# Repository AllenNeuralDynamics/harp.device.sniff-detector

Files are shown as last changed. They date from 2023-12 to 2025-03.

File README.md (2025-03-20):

Analog Front-End for an implanted 22KOhm thermistor.

## Features:
* 1Hz highpass filter
* 1KHz lowpass filter
* Vout = 1.65 + 100\*Vin
* Common mode thermistor input filtering
* Common mode supply voltage filtering

## Wiring Diagram
TODO

## Additional Parts
These parts aren't part of the PCBA, but they are required for a complete sensing solution:

* 22kOhm thermsistor PN: GAG22K7MCD419 [digikey link](https://www.digikey.com/en/products/detail/te-connectivity-measurement-specialties/GAG22K7MCD419/5277253)
* Flexible 2-conductor 36AWG Shielded TAU cable PN: TAU-3607.02 [link](https://www.micronmeters.com/product/tau-cable-36-awg)
* 2-Pin Molex Connector Plug PN: 0533984002 ([link](https://www.digikey.com/en/products/detail/molex/0533984002/15622916))
* 2-Pin Molex Connector Socket PN: 0151340206 ([link](https://www.digikey.com/en/products/detail/molex/0151340206/6198199))

### Old Connectors
These connectors are no longer used:
* 2-pin Mill Max Connector pins PN: 850-10-002-20-001000 [digikey link](https://www.digikey.com/en/products/detail/mill-max-manufacturing-corp/800-10-002-20-001000/7762570)
* 2-socket Mill Max Connector socket PN: 801-47-002-10-012000 [digikey link](https://www.digikey.com/en/products/detail/mill-max-manufacturing-corp/801-47-002-10-012000/7364072)

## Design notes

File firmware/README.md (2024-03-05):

## Setting up the Build Environment

### Install Submodules
This project uses [Harp Core RP2040](https://github.com/AllenNeuralDynamics/harp.core.rp2040) and [etl](https://github.com/ETLCPP/etl/tree/master) libraries as submodules.
Install it with:
````
git submodule update --init
````

### Install Pico SDK
This project uses the [Pico SDK](https://github.com/raspberrypi/pico-sdk/tree/master).
The SDK needs to be downloaded and installed to a known folder on your PC.
Note that the PICO SDK also contains submodules (including TinyUSB), so you must ensure that they are also fetched with:
````
git clone git clone git@github.com:raspberrypi/pico-sdk.git
git submodule update --init --recursive
````

### Point to Pico SDK
Recommended, but optional: define the `PICO_SDK_PATH` environment variable to point to the location where the pico-sdk was downloaded. i.e:
````
PICO_SDK_PATH=/home/username/projects/pico-sdk
````
On Linux, it may be preferrable to put this in your `.bashrc` file.

## Compiling the Firmware

### Without an IDE
From this directory, create a directory called build, enter it, and invoke cmake with:
````
mkdir build
cd build
cmake ..
````
If you did not define the `PICO_SDK_PATH` as an environment variable, you must pass it in here like so:
````
mkdir build
cd build
cmake -DPICO_SDK_PATH=/path/to/pico-sdk ..
````
After this point, you can invoke the auto-generated Makefile with `make`

## Flashing the Firmware
Press-and-hold the Pico's BOOTSEL button and power it up (i.e: plug it into usb).
At this point you do one of the following:
* drag-and-drop the created **\*.uf2** file into the mass storage device that appears on your pc.
* flash with [picotool](https://github.com/raspberrypi/picotool)

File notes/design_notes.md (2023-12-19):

## References
* [Shibaura Thermistors](https://www.shibauraelectronics.com/pdf/shibaura_products_catalog.pdf)
    * Overview of thermistor principles
* [Thermistor Temperature Sensing System](https://www.analog.com/en/analog-dialogue/articles/thermistor-temperature-sensing-system-part-1.html)
* [Thermistor Interfacing](https://www.analog.com/media/en/training-seminars/design-handbooks/transducer-interfacing-handbook/Chapter9.pdf)
* [QR Code Generator](https://www.the-qrcode-generator.com/)
* [Hammond Manufacturing enclosure dimensions](https://www.hammfg.com/files/parts/pdf/1455C801.pdf)
## Self-Heating Strategy References
* [LM134 Datasheet](https://www.analog.com/media/en/technical-documentation/data-sheets/134sfc.pdf)
    * Constant current source for self-heating strategy (See "Zero Temperature Coefficient Current Source".)
* [Thermal Anemometers](http://www.fonema.se/anemom/anemom.html)
* [Constant Current Hot-Wire Anemometer](https://forum.allaboutcircuits.com/threads/constant-current-hot-wire-anemometer.63204/page-2#post-432202)
* [Thermistor for Simple Breath Detector](https://forum.allaboutcircuits.com/threads/thermistor-for-simple-breath-detector.173203/)
* [Differential and Common Mode Noise](https://www.murata.com/~/media/webrenewal/products/emc/emifil/knowhow/26to30.ashx)

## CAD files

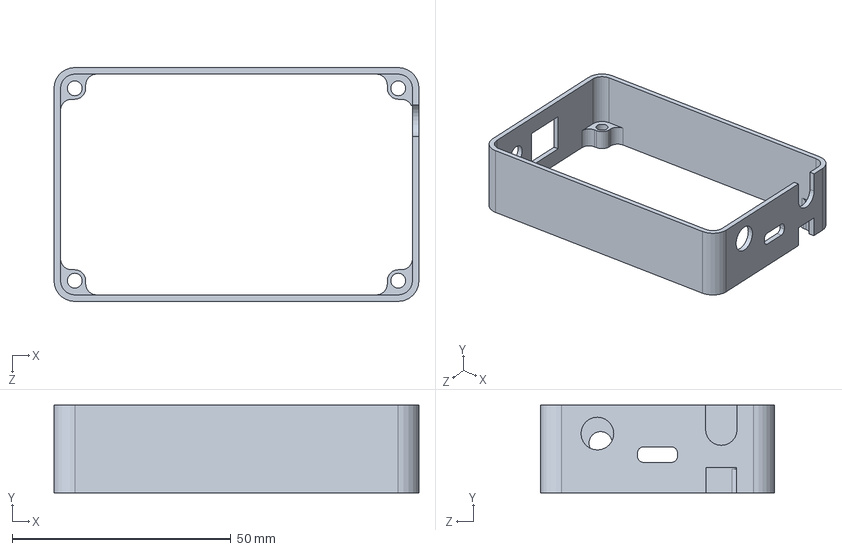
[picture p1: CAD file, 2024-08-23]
hardware/enclosure/cads/solidworks/sniff_detector_enclosure.SLDPRT
83.5 x 20.1 x 53.5 mm

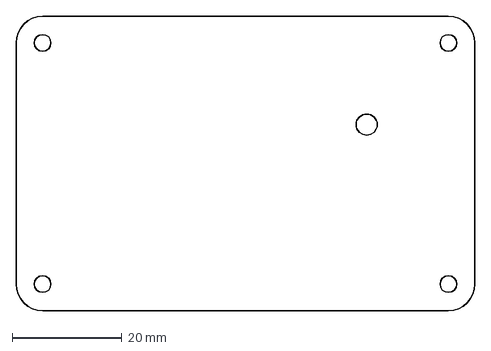
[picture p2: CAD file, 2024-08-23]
hardware/enclosure/exports/dxfs/sniff_detector_enclosure_lid_top_offset.DXF
83.7 x 53.7 mm

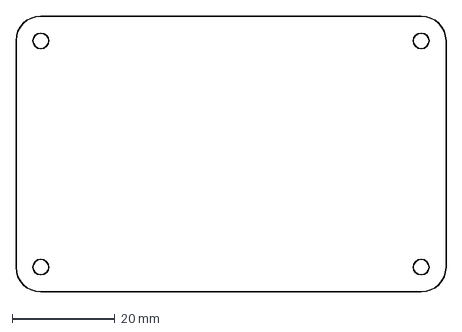
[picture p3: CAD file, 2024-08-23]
hardware/enclosure/exports/dxfs/sniff_detector_enclosure_lid_bottom_offset.DXF
83.7 x 53.7 mm

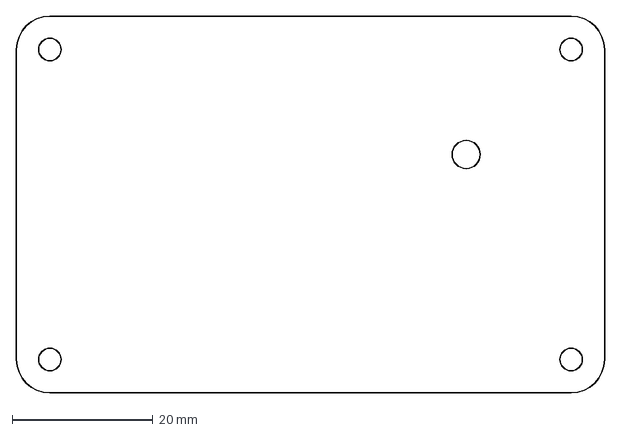
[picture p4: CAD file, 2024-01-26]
hardware/enclosure/exports/dxfs/sniff_detector_enclosure_lid_top.DXF
83.5 x 53.5 mm

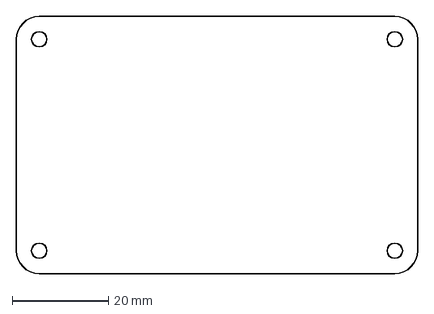
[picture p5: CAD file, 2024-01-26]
hardware/enclosure/exports/dxfs/sniff_detector_enclosure_lid_bottom.DXF
83.5 x 53.5 mm

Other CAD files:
hardware/enclosure/exports/stls/sniff_detector_sides_enclosure.STL

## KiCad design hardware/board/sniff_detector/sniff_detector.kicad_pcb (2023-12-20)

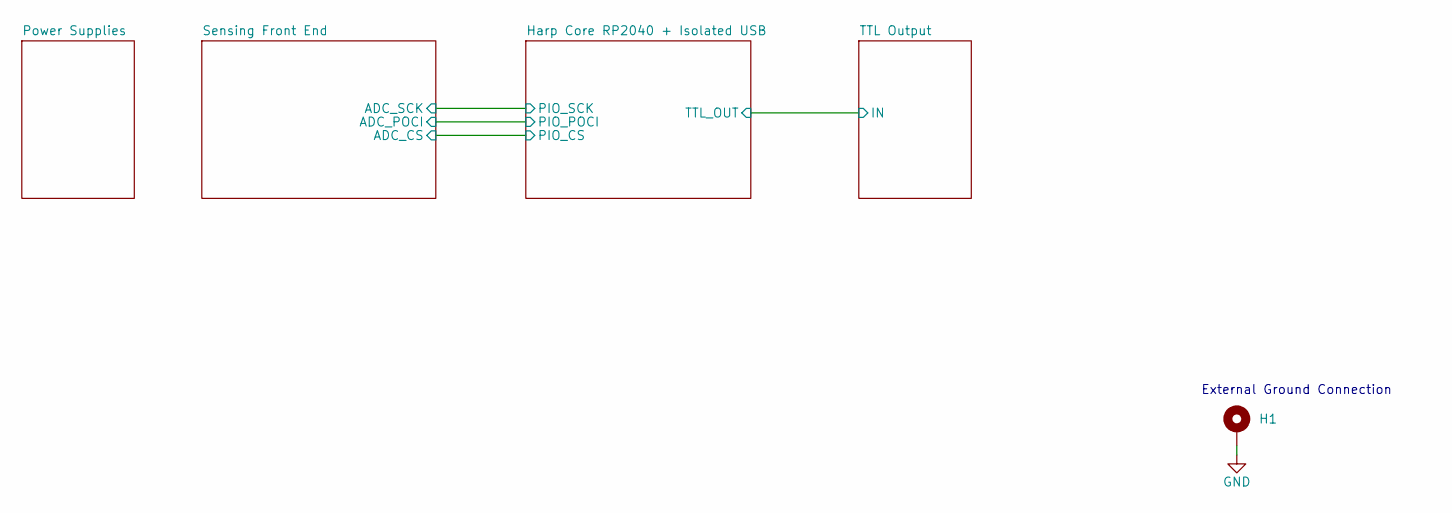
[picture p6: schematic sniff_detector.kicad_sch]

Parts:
H1: MountingHole_Pad; Terminal_Keystone_779x_EdgeMount_Horizontal

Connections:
GND: H1.1; also elsewhere on the board

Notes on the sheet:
External Ground Connection

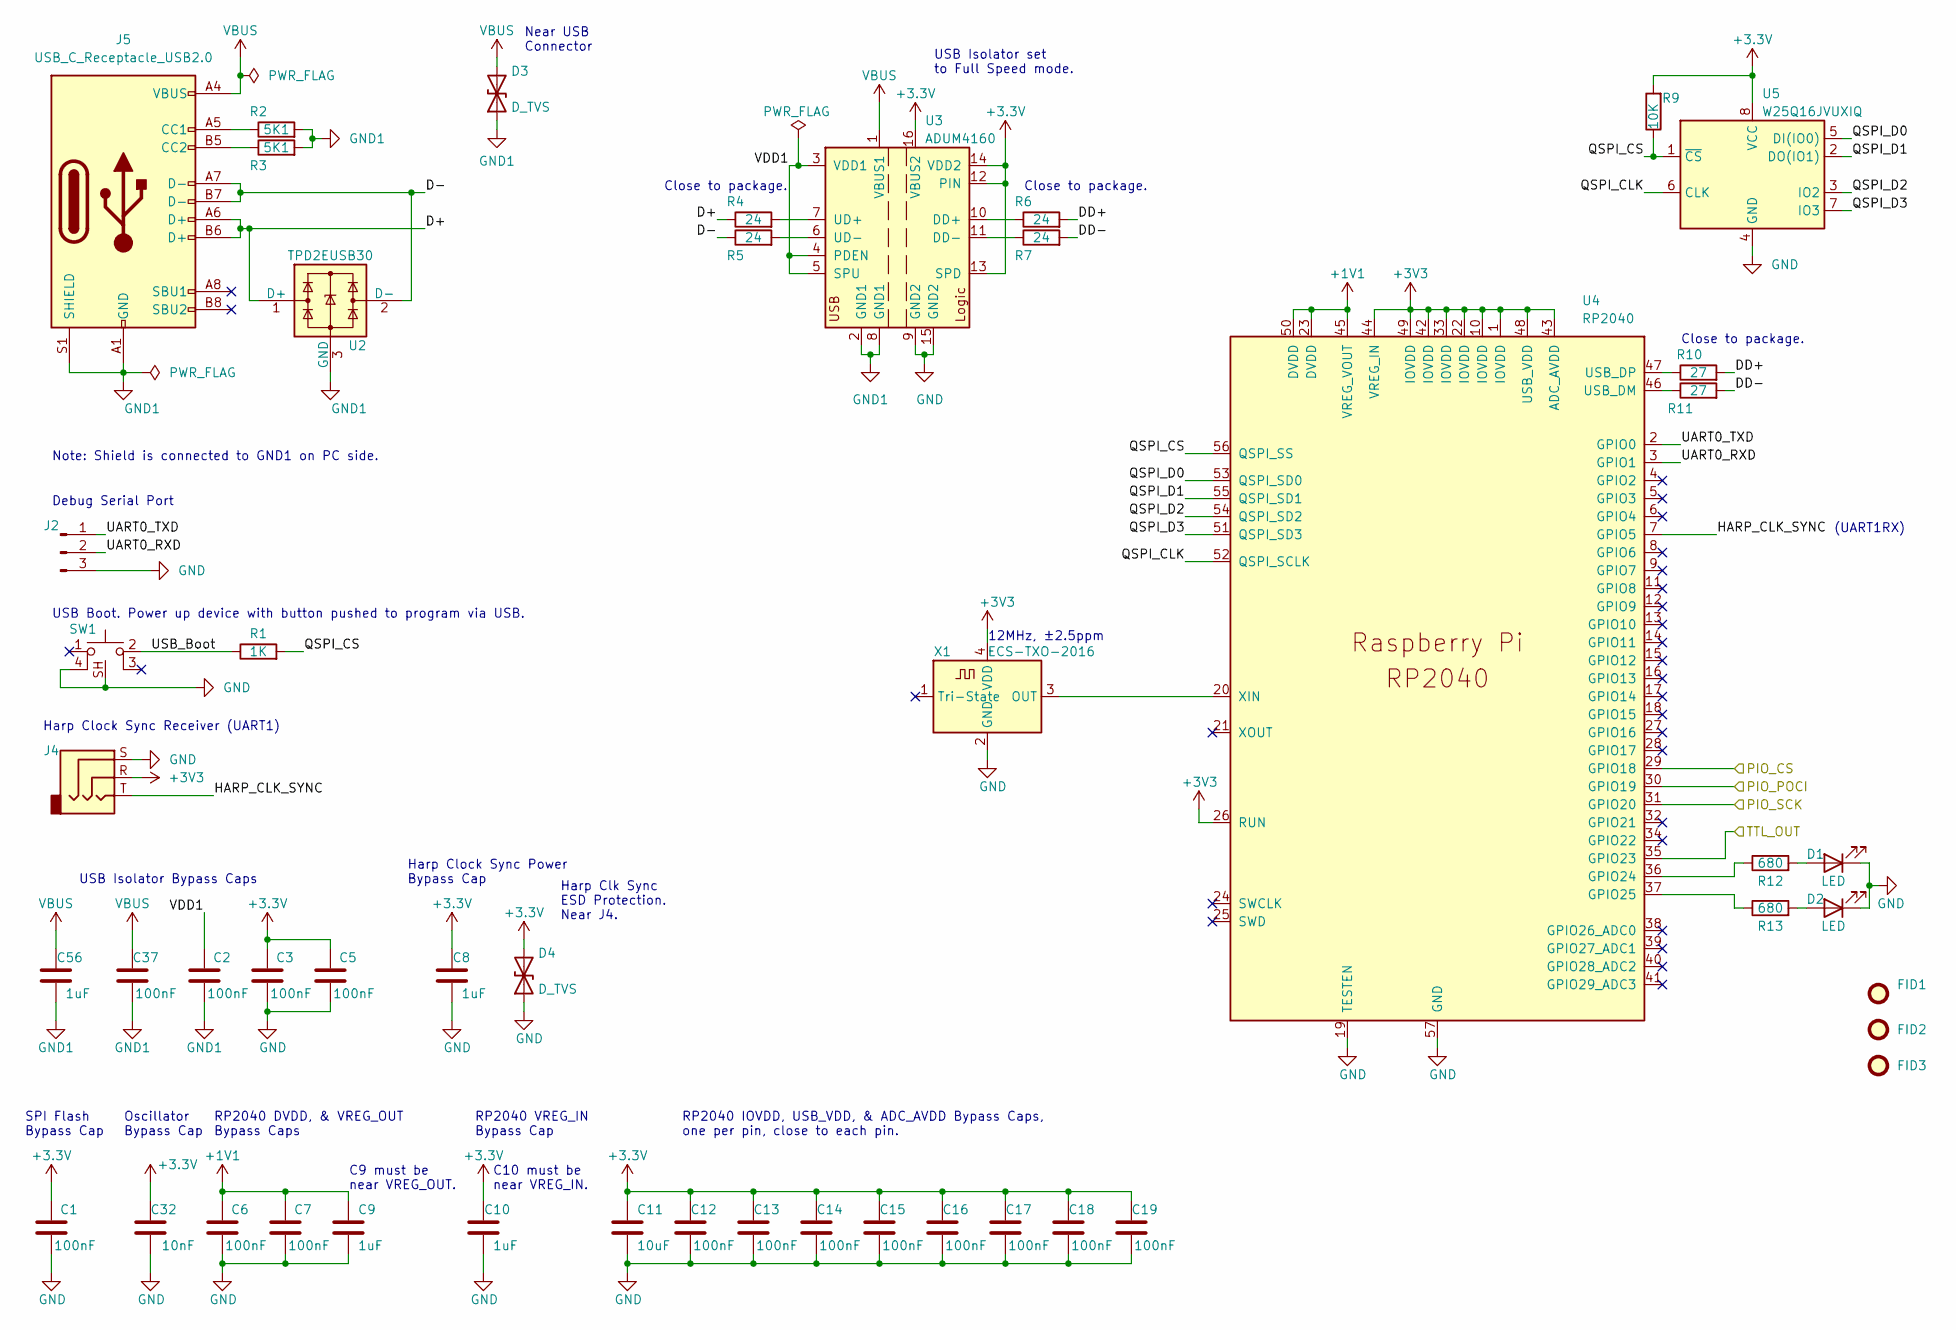
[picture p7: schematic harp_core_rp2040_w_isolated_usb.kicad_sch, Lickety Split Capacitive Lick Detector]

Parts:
C1, C2, C3, C5, C6, C7, C12, C13, C14, C15, C16, C17, C18, C19, C37: 100nF; C_0402_1005Metric; Rated Voltage 16V; Tolerance 10%
C8, C9, C10, C56: 1uF; C_0402_1005Metric; Rated Voltage 35V; Voltage 35V
C11: 10uF; C_0603_1608Metric; Rated Voltage 25V; Tolerance 10%
C32: 10nF; C_0402_1005Metric; Rated Voltage 25V; Tolerance 10%
D1, D2: LED; LED_0603_1608Metric_Pad1.05x0.95mm_HandSolder
D3, D4: D_TVS; D_0402_1005Metric
FID1, FID2, FID3: Fiducial; Fiducial_0.5mm_Mask1mm
J2: Conn_01x03_Male; PinHeader_1x03_P2.54mm_Vertical
J4: AudioJack3; Jack_3.5mm_CUI_SJ-3523-SMT_Horizontal
J5: USB_C_Receptacle_USB2.0; USB_C_Receptacle_JAE_DX07S016JA1R1500
R1: 1K; R_0402_1005Metric; Tolerance 1%
R2, R3: 5K1; R_0402_1005Metric; Tolerance 1%
R4, R5, R6, R7: 24; R_0402_1005Metric; Tolerance 1%
R9: 10K; R_0402_1005Metric
R10, R11: 27; R_0402_1005Metric; Tolerance 1%
R12, R13: 680; R_0402_1005Metric; Tolerance 1%
SW1: SW_Push_1P1T-SH_NO_Vertical_Wuerth_WS-TASV
U2: TPD2EUSB30; Texas_DRT-3
U3: ADUM4160; SOIC-16W_7.5x10.3mm_P1.27mm
U4: RP2040; RP2040-QFN-56
U5: W25Q16JVUXIQ; Winbond-8USON-2x3mm
X1: ECS-TXO-2016; Crystal_SMD_2016-4Pin_2.0x1.6mm; Tolerance ±2.5ppm

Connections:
+1V1: C6.2, C7.2, C9.1, U4.23 (DVDD), U4.45 (VREG_VOUT), U4.50 (DVDD)
/Harp Core RP2040 + Isolated USB/D+: J5.A6 (D+), J5.B6 (D+), R4.1, U2.1 (D+)
/Harp Core RP2040 + Isolated USB/D-: J5.A7 (D-), J5.B7 (D-), R5.1, U2.2 (D-)
/Harp Core RP2040 + Isolated USB/DD+: R6.2, R10.2
/Harp Core RP2040 + Isolated USB/DD-: R7.2, R11.2
/Harp Core RP2040 + Isolated USB/HARP_CLK_SYNC: J4.T, U4.7 (GPIO5)
/Harp Core RP2040 + Isolated USB/PIO_CS: U4.29 (GPIO18); also elsewhere on the board
/Harp Core RP2040 + Isolated USB/PIO_POCI: U4.30 (GPIO19); also elsewhere on the board
/Harp Core RP2040 + Isolated USB/PIO_SCK: U4.31 (GPIO20); also elsewhere on the board
/Harp Core RP2040 + Isolated USB/QSPI_CLK: U4.52 (QSPI_SCLK), U5.6 (CLK)
/Harp Core RP2040 + Isolated USB/QSPI_CS: R1.2, R9.1, U4.56 (QSPI_SS), U5.1 (~CS)
/Harp Core RP2040 + Isolated USB/QSPI_D0: U4.53 (QSPI_SD0), U5.5 (DI(IO0))
/Harp Core RP2040 + Isolated USB/QSPI_D1: U4.55 (QSPI_SD1), U5.2 (DO(IO1))
/Harp Core RP2040 + Isolated USB/QSPI_D2: U4.54 (QSPI_SD2), U5.3 (IO2)
/Harp Core RP2040 + Isolated USB/QSPI_D3: U4.51 (QSPI_SD3), U5.7 (IO3)
/Harp Core RP2040 + Isolated USB/TTL_OUT: U4.35 (GPIO23); also elsewhere on the board
/Harp Core RP2040 + Isolated USB/UART0_RXD: J2.2, U4.3 (GPIO1)
/Harp Core RP2040 + Isolated USB/UART0_TXD: J2.1, U4.2 (GPIO0)
/Harp Core RP2040 + Isolated USB/USB_Boot: R1.1, SW1.2
/Harp Core RP2040 + Isolated USB/VDD1: C2.2, U3.3 (VDD1), U3.4 (PDEN), U3.5 (SPU)
GND: C1.1, C3.1, C5.1, C6.1, C7.1, C8.2, C9.2, C10.2, C11.2, C12.1, C13.1, C14.1, C15.1, C16.1, C17.1, C18.1, C19.1, C32.1, D1.1 (K), D2.1 (K), D4.1 (A1), J2.3, J4.S, SW1.4, SW1.SH, U3.9 (GND2), U3.15 (GND2), U4.19 (TESTEN), U4.57 (GND), U5.4 (GND), X1.2 (GND); also elsewhere on the board
GND1: C2.1, C37.1, C56.2, D3.1 (A1), J5.A1 (GND), J5.A12 (GND), J5.B1 (GND), J5.B12 (GND), J5.S1 (SHIELD), R2.2, R3.2, U2.3 (GND), U3.2 (GND1), U3.8 (GND1)
unnamed: D1.2 (A), R12.2
unnamed: D2.2 (A), R13.2
unnamed: J5.A5 (CC1), R2.1
unnamed: J5.B5 (CC2), R3.1
unnamed: R6.1, U3.10 (DD+)
unnamed: R7.1, U3.11 (DD-)
unnamed: R4.2, U3.7 (UD+)
unnamed: R5.2, U3.6 (UD-)
unnamed: R12.1, U4.36 (GPIO24)
unnamed: R13.1, U4.37 (GPIO25)
unnamed: R11.1, U4.46 (USB_DM)
unnamed: R10.1, U4.47 (USB_DP)
unnamed: U4.20 (XIN), X1.3 (OUT)
VBUS: C37.2, C56.1, D3.2 (A2), J5.A4 (VBUS), J5.A9 (VBUS), J5.B4 (VBUS), J5.B9 (VBUS), U3.1 (VBUS1)

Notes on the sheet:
Close to package.
Near USB Connector
(UART1RX)
Harp Clk Sync ESD Protection. Near J4.
RP2040 VREG_IN Bypass Cap
Oscillator Bypass Cap
Harp Clock Sync Power Bypass Cap
C10 must be near VREG_IN.
RP2040 DVDD, & VREG_OUT Bypass Caps
Debug Serial Port
USB Boot. Power up device with button pushed to program via USB.
C9 must be near VREG_OUT.
Harp Clock Sync Receiver (UART1)
12MHz, ±2.5ppm
Note: Shield is connected to GND1 on PC side.
RP2040 IOVDD, USB_VDD, & ADC_AVDD Bypass Caps, one per pin, close to each pin.
USB Isolator Bypass Caps
SPI Flash Bypass Cap
USB Isolator set to Full Speed mode.

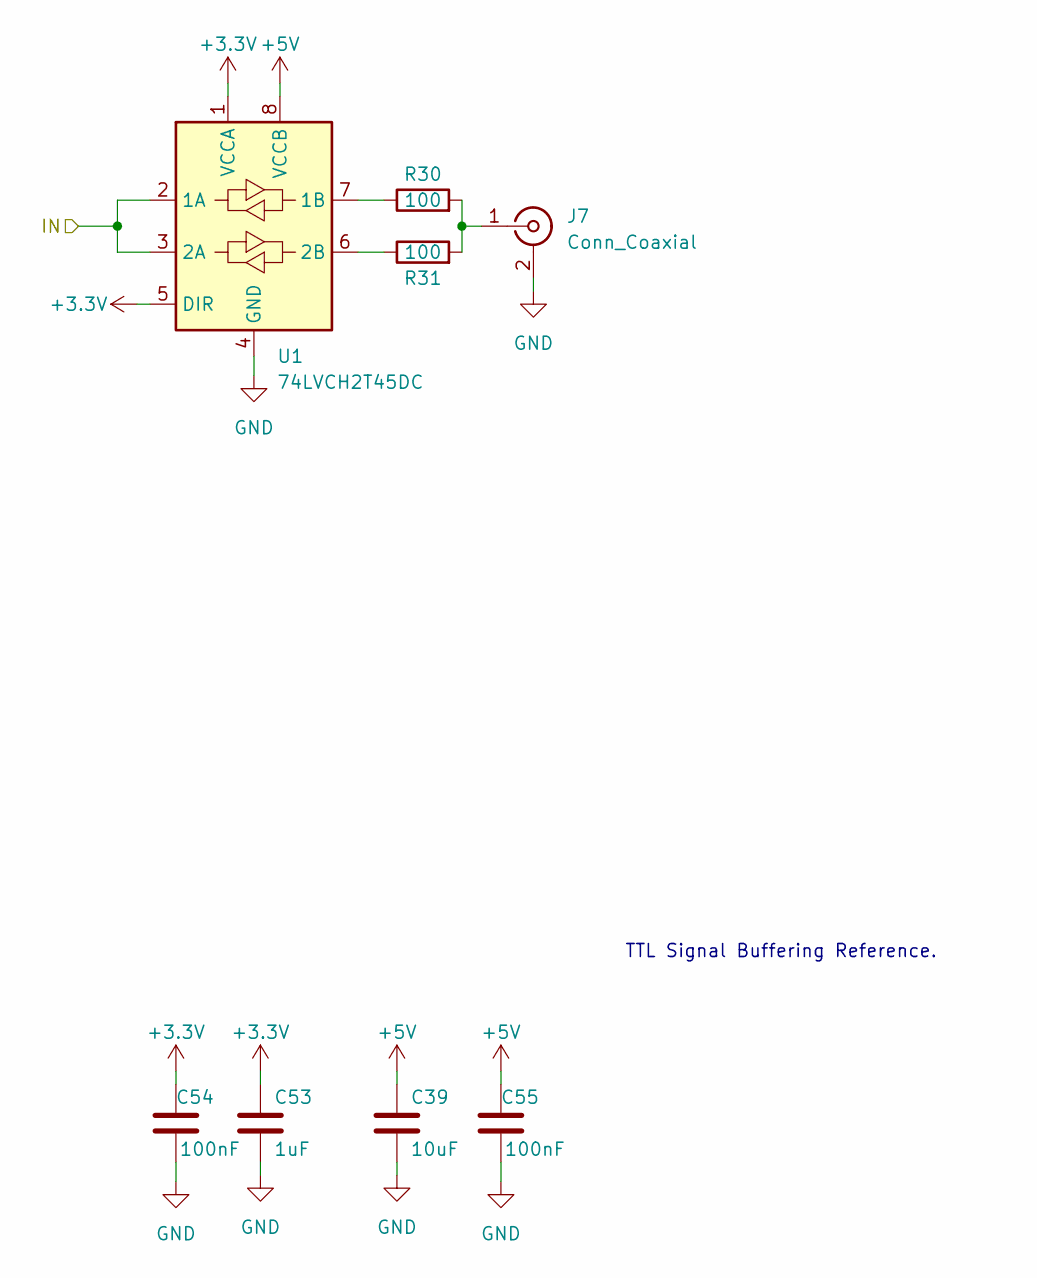
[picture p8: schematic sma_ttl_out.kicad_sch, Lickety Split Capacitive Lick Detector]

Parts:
C39: 10uF; C_0603_1608Metric; Rated Voltage 25V; Tolerance 10%
C53: 1uF; C_0402_1005Metric; Rated Voltage 35V; Voltage 35V
C54, C55: 100nF; C_0402_1005Metric; Rated Voltage 16V; Tolerance 10%
J7: Conn_Coaxial; SMA_TE_Connectivity_CONSMA002-SMD-G-T_Horizontal
R30, R31: 100; R_0603_1608Metric_Pad0.98x0.95mm_HandSolder; Tolerance 1%
U1: 74LVCH2T45DC; VSSOP-8_2.3x2mm_P0.5mm

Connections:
+5V: C39.1, C55.2, U1.8 (VCCB); also elsewhere on the board
/Harp Core RP2040 + Isolated USB/TTL_OUT: U1.2 (1A), U1.3 (2A); also elsewhere on the board
GND: C39.2, C53.2, C54.1, C55.1, J7.2 (Ext), U1.4 (GND); also elsewhere on the board
unnamed: J7.1 (In), R30.2, R31.2
unnamed: R30.1, U1.7 (1B)
unnamed: R31.1, U1.6 (2B)

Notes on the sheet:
TTL Signal Buffering Reference.

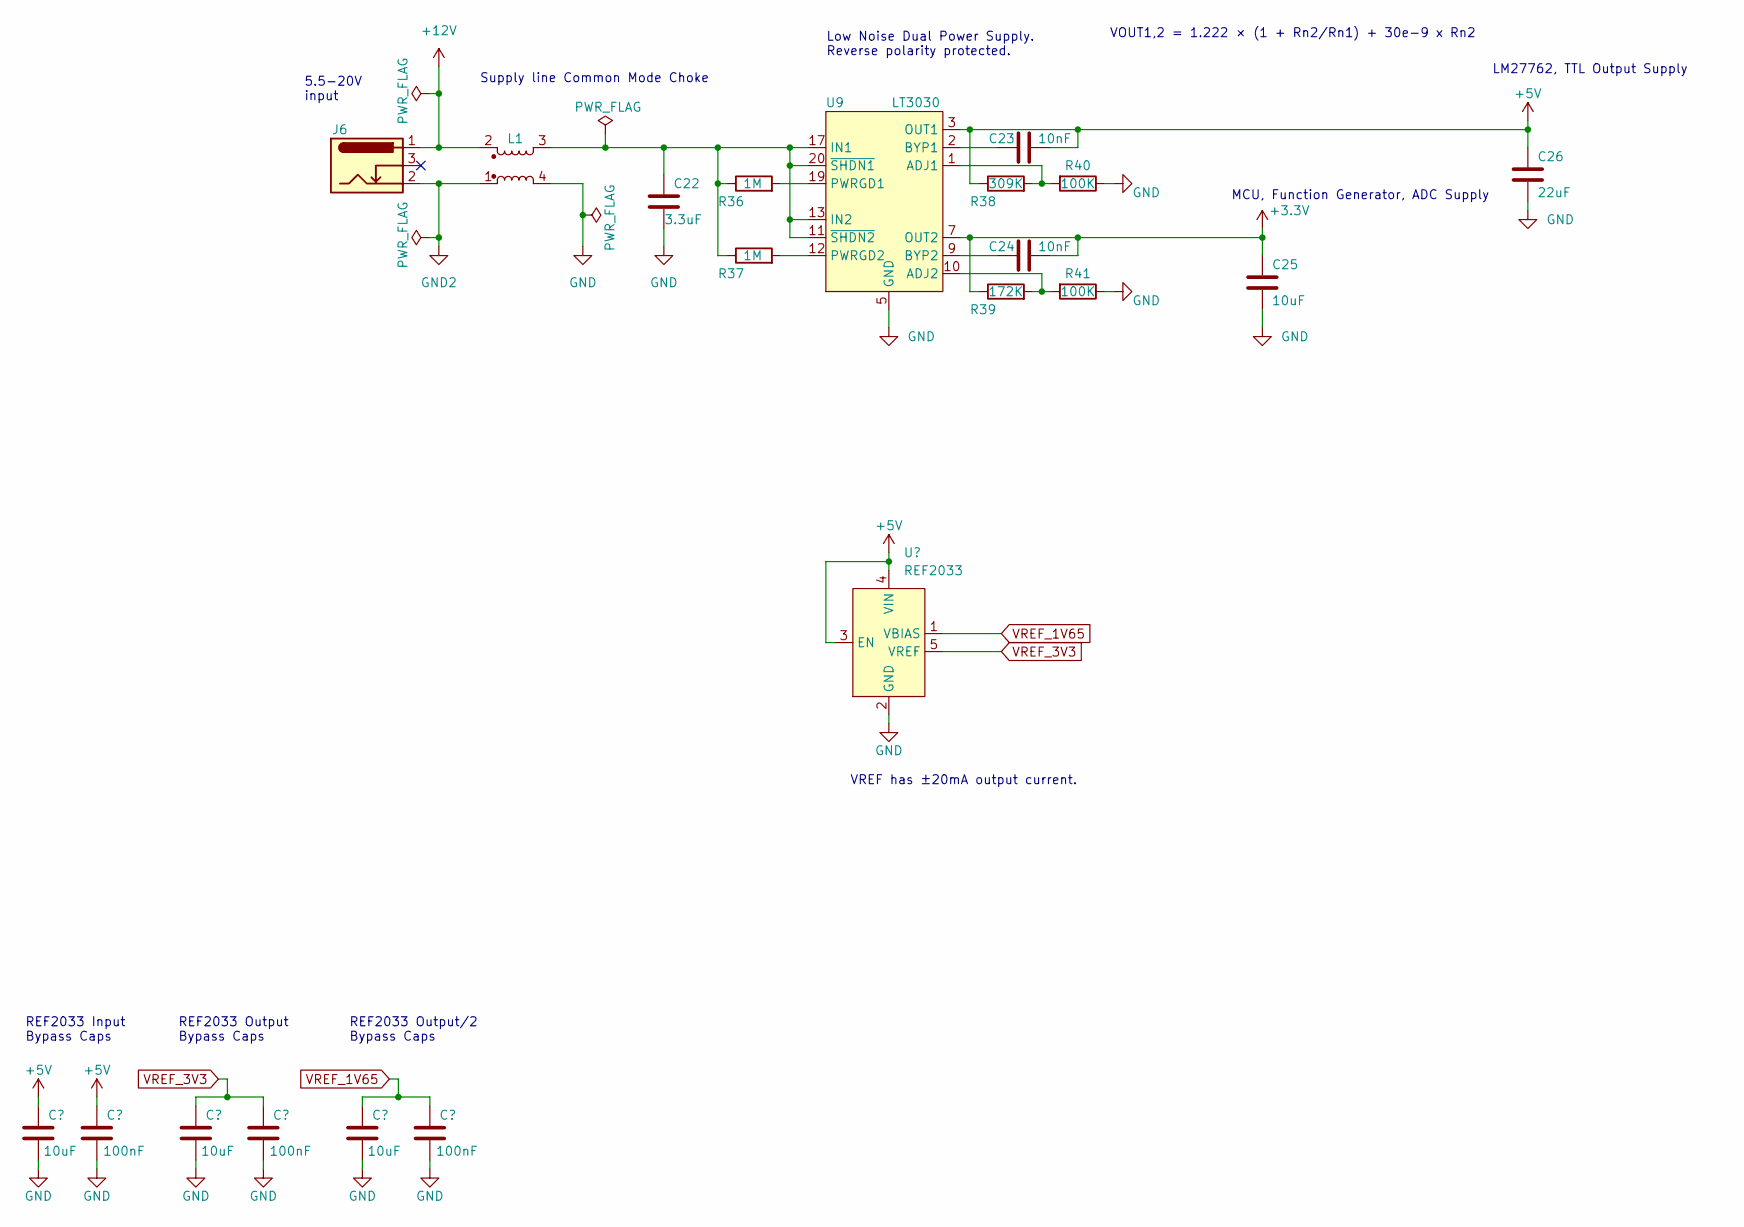
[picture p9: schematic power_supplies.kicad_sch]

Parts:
C22: 3.3uF; C_0805_2012Metric; Rated Voltage 25V; Tolerance 10%
C23, C24: 10nF; C_0402_1005Metric; Rated Voltage 25V; Tolerance 10%
C25: 10uF; C_0603_1608Metric; Rated Voltage 25V; Tolerance 10%
C26: 22uF; C_0805_2012Metric; Rated Voltage 25V; Voltage 25V
C35, C38, C41: 10uF; C_0603_1608Metric; Tolerance 10%; Voltage 25V
C36, C40, C42: 100nF; C_0402_1005Metric; Tolerance 10%; Voltage 16V
J6: Barrel_Jack_Switch; BarrelJack_CUI_PJ-102AH_Horizontal
L1: L_Coupled_1423; L_CommonModeChoke_TDKCorporation_1210
R36, R37: 1M; R_0402_1005Metric; Tolerance 1%
R38: 309K; R_0402_1005Metric; Tolerance 0.1%
R39: 172K; R_0402_1005Metric; Tolerance 1%
R40, R41: 100K; R_0402_1005Metric; Tolerance 0.1%
U8: REF2033; SOT-23-5
U9: LT3030; ETSSOP-20-1EP_4.4x6.5mm_P0.65mm_EP3x4.2mm

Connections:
+5V: C23.1, C26.1, C35.1, C36.2, R38.1, U8.3 (EN), U8.4 (VIN), U9.3 (OUT1), U9.4 (OUT1); also elsewhere on the board
+12V: J6.1, L1.2
GND: C22.2, C25.2, C26.2, C35.2, C36.1, C38.2, C40.1, C41.2, C42.1, L1.4, R40.1, R41.1, U8.2 (GND), U9.5 (GND), U9.6 (GND), U9.15 (GND), U9.16 (GND), U9.21 (GND); also elsewhere on the board
GND2: J6.2, L1.1
IN1: C22.1, L1.3, R36.1, R37.1, U9.11 (~SHDN2), U9.13 (IN2), U9.14 (IN2), U9.17 (IN1), U9.18 (IN1), U9.20 (~SHDN1)
unnamed: R38.2, R40.2, U9.1 (ADJ1)
unnamed: R39.2, R41.2, U9.10 (ADJ2)
unnamed: C23.2, U9.2 (BYP1)
unnamed: C24.2, U9.9 (BYP2)
unnamed: R36.2, U9.19 (PWRGD1)
unnamed: R37.2, U9.12 (PWRGD2)
VREF_1V65: C41.1, C42.2, U8.1 (VBIAS); also elsewhere on the board
VREF_3V3: C38.1, C40.2, U8.5 (VREF); also elsewhere on the board

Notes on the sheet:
REF2033 Input Bypass Caps
REF2033 Output/2 Bypass Caps
MCU, Function Generator, ADC Supply
5.5-20V input
REF2033 Output Bypass Caps
VOUT1,2 = 1.222 × (1 + Rn2/Rn1) + 30e-9 x Rn2
Supply line Common Mode Choke
VREF has ±20mA output current.
Low Noise Dual Power Supply. Reverse polarity protected.
LM27762, TTL Output Supply

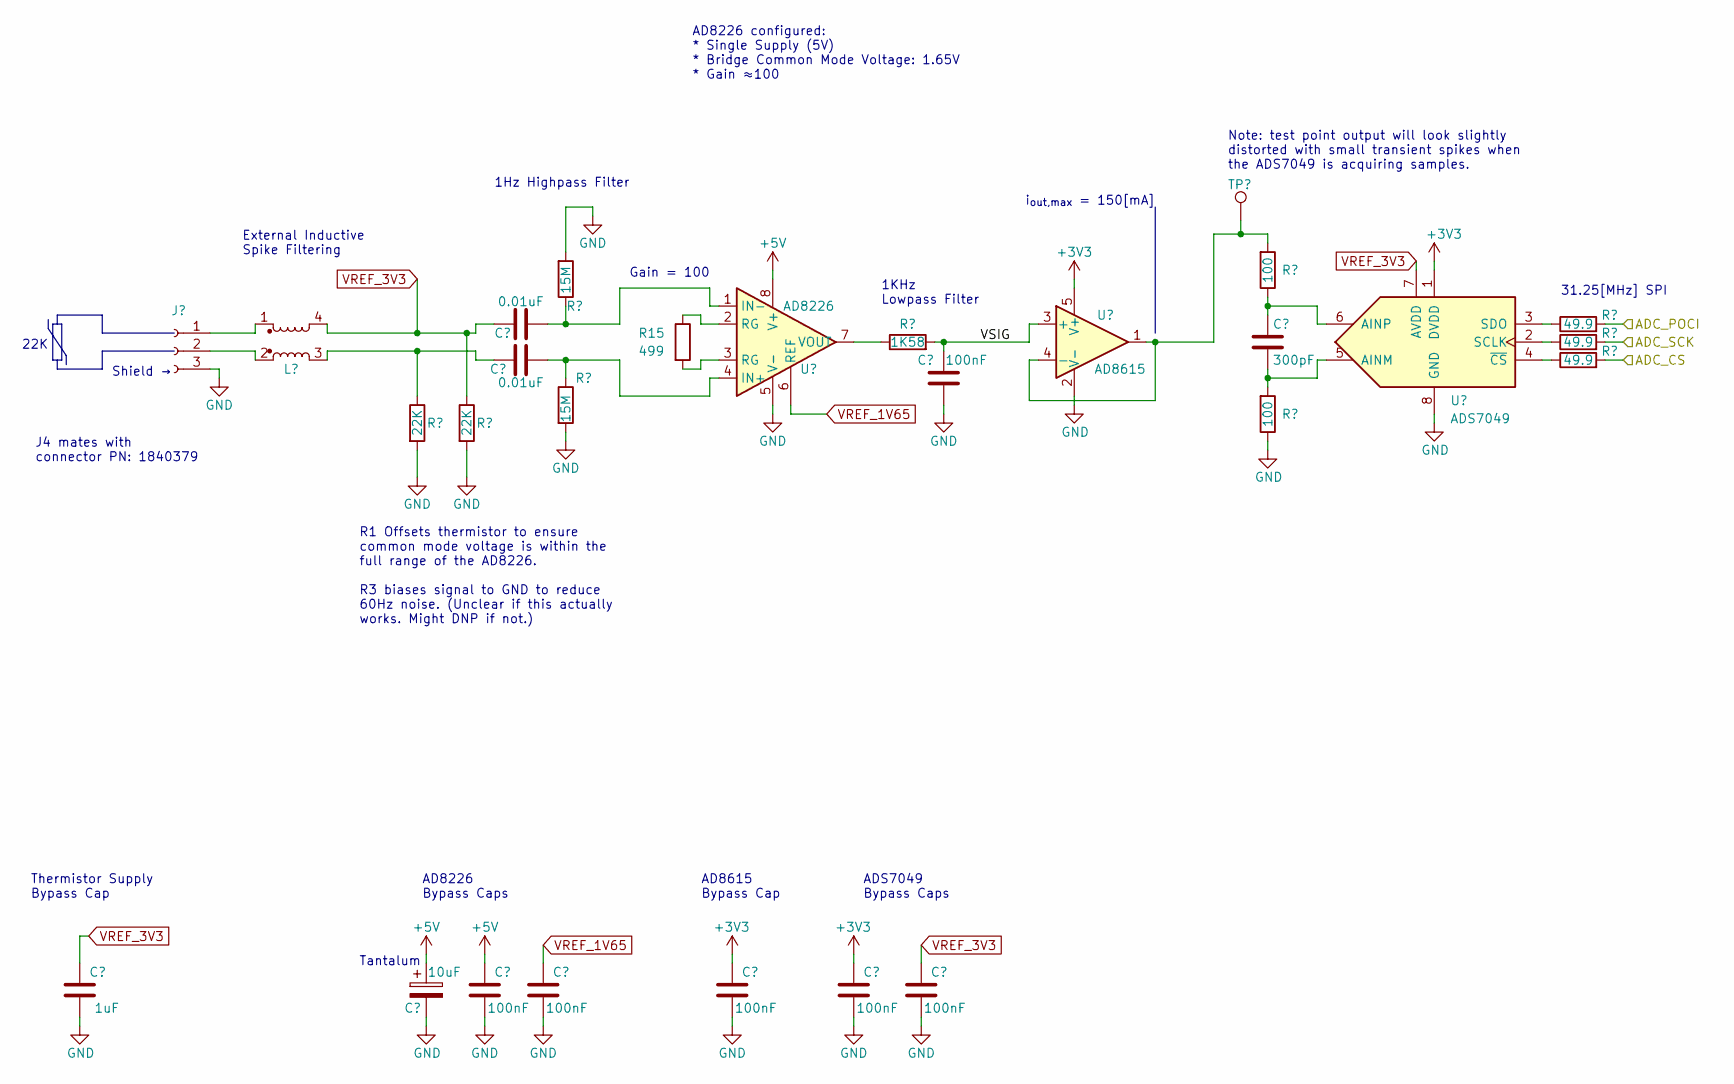
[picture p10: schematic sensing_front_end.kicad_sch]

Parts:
C4: 1uF; C_0402_1005Metric; Voltage 35V; Rated Voltage 35V
C20: 10uF; C_0805_2012Metric; Rated Voltage 10V; Tolerance 20%
C21, C29, C30, C31, C33: 100nF; C_0402_1005Metric; Rated Voltage 16V; Tolerance 10%
C27, C28: 0.01uF; C_1206_3216Metric; Tolerance 1%
C34: 100nF; C_0402_1005Metric; Tolerance 10%; Voltage 16V
C52: 300pF; C_0402_1005Metric; Tolerance 1%
J1: Conn_01x03_Female; PhoenixContact_MC_1,5_3-G-3.5_1x03_P3.50mm_Horizontal
L2: L_Coupled_1423; L_CommonModeChoke_TDKCorporation_1210
R8, R18: 22K; R_0603_1608Metric; Tolerance 0.1%
R14, R17: 15M; R_1206_3216Metric; Tolerance 1%
R15: 499; R_0603_1608Metric_Pad0.98x0.95mm_HandSolder; Tolerance 0.1%
R16: 1K58; R_0603_1608Metric; Tolerance 0.1%
R28, R29, R44: 49.9; R_0402_1005Metric
R42, R43: 100; R_0402_1005Metric; Tolerance 0.1%
TP1: TestPoint; TestPoint_Keystone_5027_Miniature
U6: AD8615; TSOT-23-5
U7: AD8226; MSOP-8_3x3mm_P0.65mm
U13: ADS7049; VSSOP-8_2.3x2mm_P0.5mm

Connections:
+5V: C20.1, C21.2, U7.8 (V+); also elsewhere on the board
/Harp Core RP2040 + Isolated USB/PIO_CS: R44.2; also elsewhere on the board
/Harp Core RP2040 + Isolated USB/PIO_POCI: R28.2; also elsewhere on the board
/Harp Core RP2040 + Isolated USB/PIO_SCK: R29.2; also elsewhere on the board
/Sensing Front End/VSIG: C34.1, R16.2, U6.3 (+)
GND: C4.1, C20.2, C21.1, C29.1, C30.1, C31.1, C33.1, C34.2, J1.3, R8.2, R14.2, R17.2, R18.2, R42.1, U6.2 (V-), U7.5 (V-), U13.8 (GND); also elsewhere on the board
unnamed: C28.1, L2.3, R8.1
unnamed: J1.1, L2.1
unnamed: J1.2, L2.2
unnamed: R15.1, U7.2 (RG)
unnamed: R15.2, U7.3 (RG)
unnamed: R43.2, TP1.1, U6.1, U6.4 (-)
unnamed: C28.2, R14.1, U7.4 (IN+)
unnamed: C27.2, R17.1, U7.1 (IN-)
unnamed: R16.1, U7.7 (VOUT)
unnamed: C52.2, R42.2, U13.5 (AINM)
unnamed: C52.1, R43.1, U13.6 (AINP)
unnamed: R29.1, U13.2 (SCLK)
unnamed: R28.1, U13.3 (SDO)
unnamed: R44.1, U13.4 (~CS)
VREF_1V65: C29.2, U7.6 (REF); also elsewhere on the board
VREF_3V3: C4.2, C27.1, C33.2, L2.4, R18.1, U13.7 (AVDD); also elsewhere on the board

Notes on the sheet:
J4 mates with connector PN: 1840379
Thermistor Supply Bypass Cap
Shield →
Tantalum
Note: test point output will look slightly distorted with small transient spikes when the ADS7049 is acquiring samples.
i_{out,max} = 150[mA]
ADS7049 Bypass Caps
R1 Offsets thermistor to ensure common mode voltage is within the full range of the AD8226. R3 biases signal to GND to reduce 60Hz noise. (Unclear if this actually works. Might DNP if not.)
1Hz Highpass Filter
AD8615 Bypass Cap
AD8226 configured: * Single Supply (5V) * Bridge Common Mode Voltage: 1.65V * Gain ≈100
31.25[MHz] SPI
External Inductive Spike Filtering
22K
AD8226 Bypass Caps
1KHz Lowpass Filter
Gain = 100

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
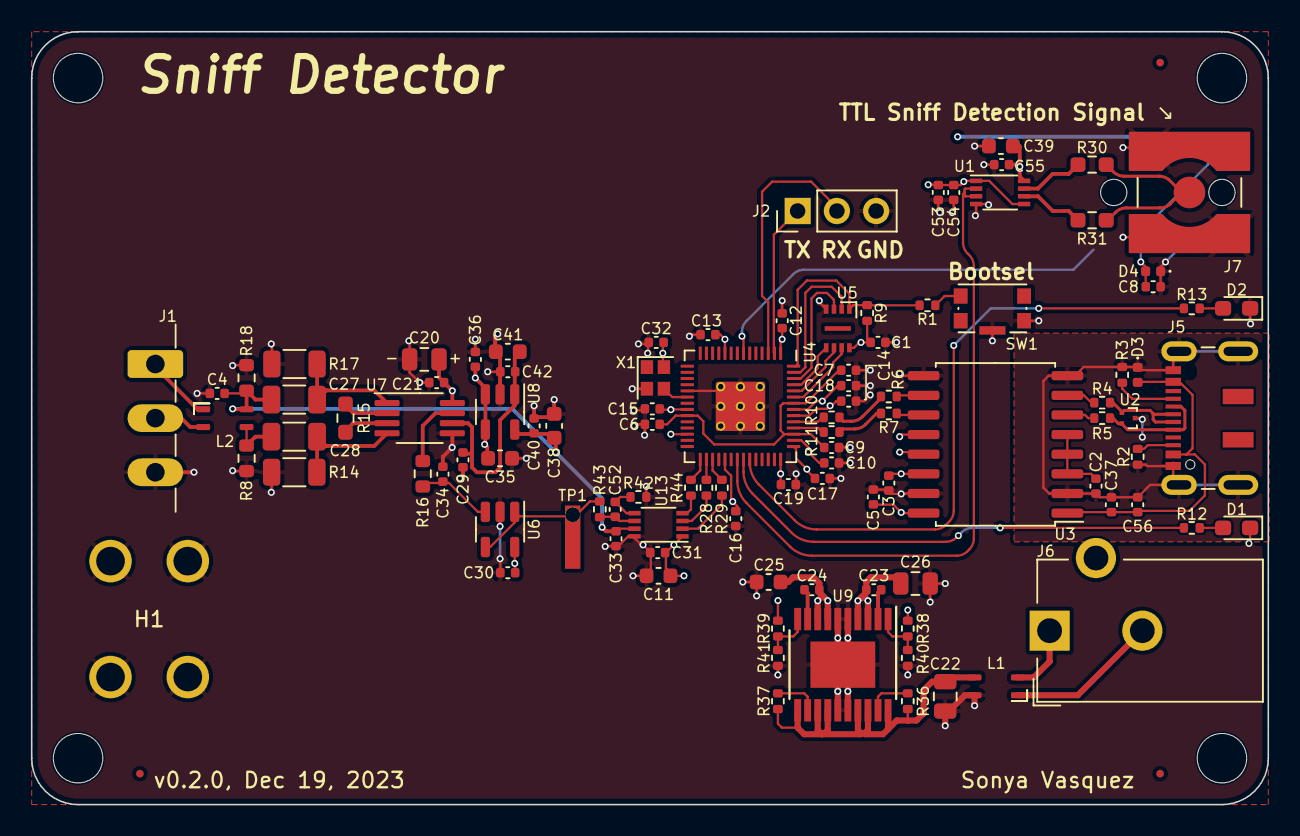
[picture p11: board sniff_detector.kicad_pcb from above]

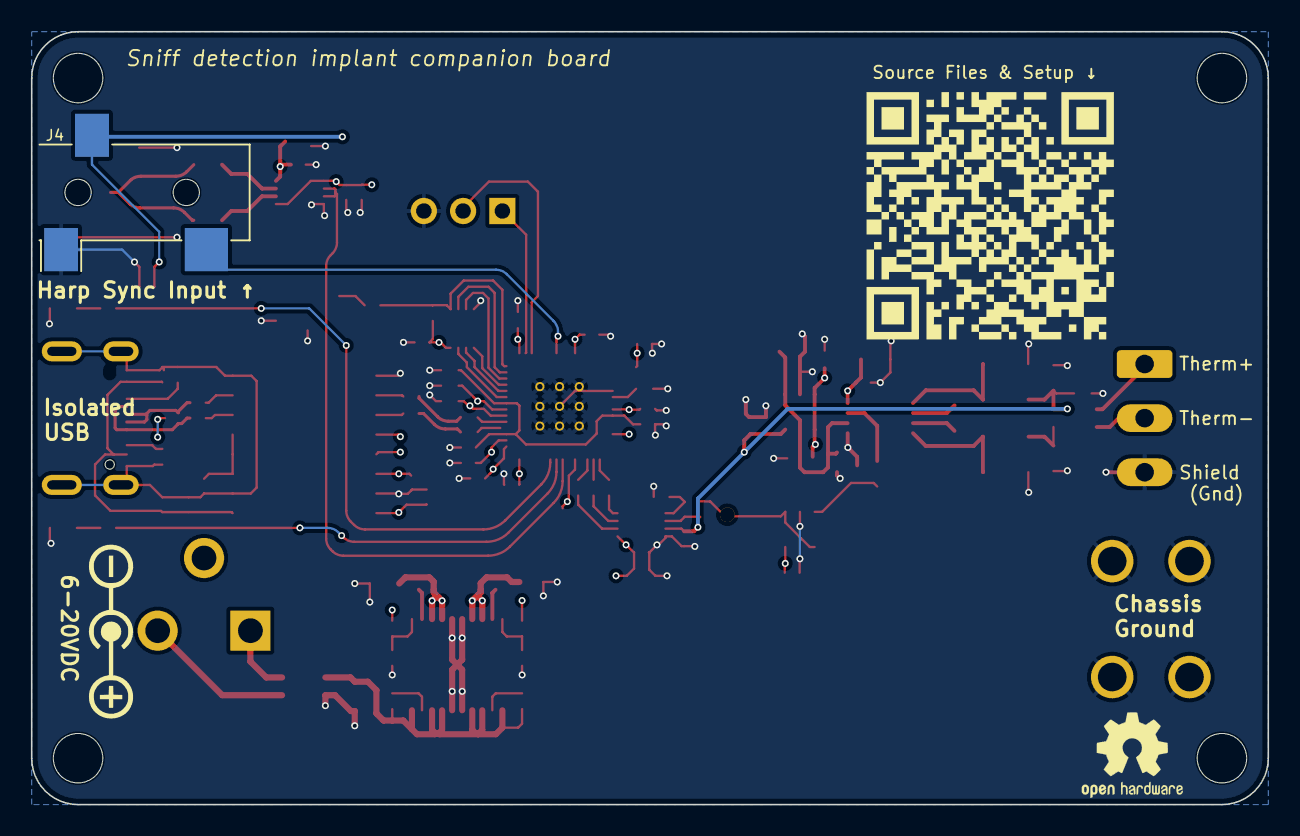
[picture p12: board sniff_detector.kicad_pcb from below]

Board: 4 copper layers, 80.0 x 50.0 mm, 109 parts (3 on the bottom side), 67 nets.

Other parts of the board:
G3: LOGO
REF1: OSHW-Logo2_7.3x6mm_SilkScreen

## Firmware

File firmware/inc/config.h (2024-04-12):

#ifndef CONFIG_H
#define CONFIG_H


#define DEFAULT_DISPATCH_FREQUENCY_HZ (0)
#define MAX_EVENT_FREQUENCY_HZ (1000)

#define UART_TX_PIN (0) // for printf-style debugging.
#define HARP_SYNC_RX_PIN (5)
#define LED0 (24)
#define LED1 (25)

// ADC
#define ADC_CS_PIN (18)
#define ADC_POCI_PIN (19)
#define ADC_SCK_PIN (20)

#define HARP_DEVICE_ID (0x0579)


#endif // CONFIG_H

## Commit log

2023-07-31 annotate schematic
    [sniff_detector.kicad_sch]
2023-08-03 annotate rev1
    [sniff_detector.kicad_sch]
2023-12-19 complete pcb v0.2
    [harp_core_rp2040_w_isolated_usb.kicad_sch, power_supplies.kicad_sch, sensing_front_end.kicad_sch, sma_ttl_out.kicad_sch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]
2023-12-20 draft firmware
    [harp_core_rp2040_w_isolated_usb.kicad_sch, power_supplies.kicad_sch, sensing_front_end.kicad_sch, sma_ttl_out.kicad_sch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]
2024-01-11 add board step file to repo
2024-01-11 add enclosure
    [sniff_detector_enclosure.SLDPRT, sniff_detector_enclosure_lid_bottom.DXF, sniff_detector_enclosure_lid_top.DXF, sniff_detector_sides_enclosure.STL]
2024-01-26 add sensor error state bitfield interpretation
2024-03-06 update default sensor dispatch rate
2024-08-23 upate lick detector enclosure
    [sniff_detector_enclosure.SLDPRT, sniff_detector_enclosure_lid_bottom_offset.DXF, sniff_detector_enclosure_lid_top_offset.DXF, sniff_detector_sides_enclosure.STL]
2024-11-10 Favor harp-tech as source of device schema
2025-03-20 Update README.md
    add new connector part numbers
